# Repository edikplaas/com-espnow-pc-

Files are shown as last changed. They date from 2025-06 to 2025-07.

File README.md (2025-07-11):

# Programmes et modèles 3D en lien avec les semelles instrumentées
Dans le cadre d'un projet de recherche concernant le développement de semelles instrumentées pour la récupèration de la dynamique du bas du corps humain, ce repository est là pour comprendre et s'aider à intégrer et programmer les semelles instrumentées.  
  
Vous retrouverez dans le dossier `Documentation` tous les guides qui expliquent les différentes étapes du projet.  
Le dossier `models` contient tous les modèles 3D des semelles.  
Les dossiers `Tests ESP NOW - PC` et `Tests RS485` servent à debugger les semelles pour comprendre les différents protocoles de communication utilisés.  
Le dossier `codePlusieursPatchs` contient les programmes les plus importants.  
  
[Lien pour tous les modèles 3D sur Onshape (seulement pour consulter)](https://cad.onshape.com/documents/ade586a7c4f5538d2dbdcdd9/w/156847e7fb1b50d2fcf403ab/e/13fe36d384e4cd3dfd326341?renderMode=0&uiState=687111e13e0cfb5b92277174)

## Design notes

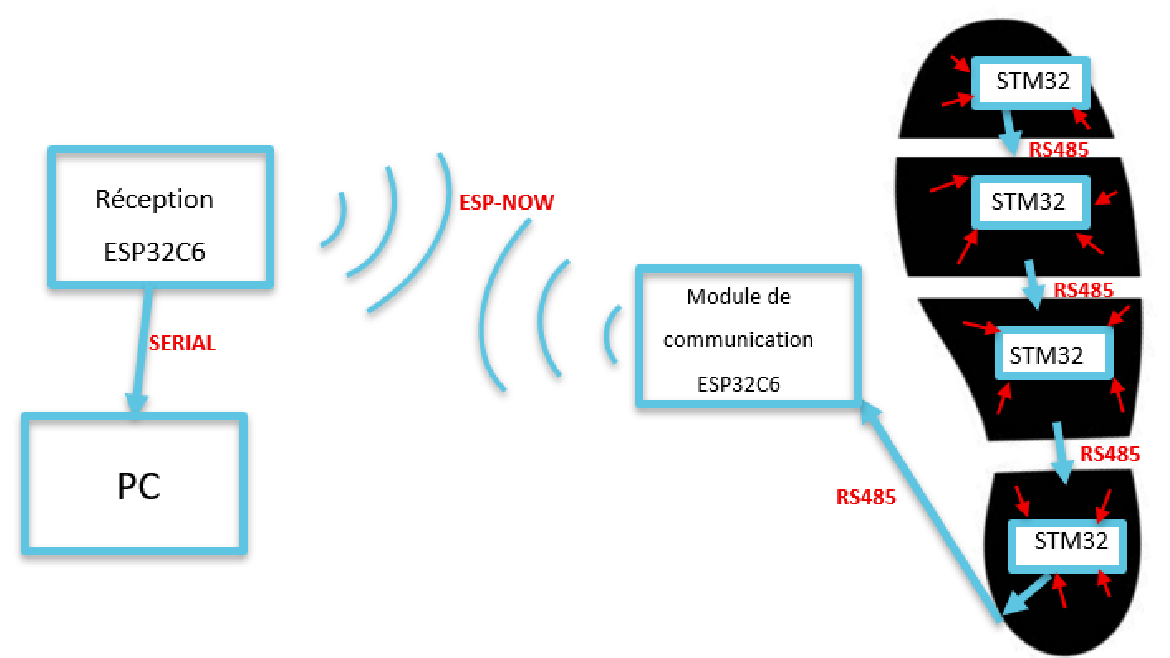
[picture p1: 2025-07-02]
Documentation/chaineCommunication.png

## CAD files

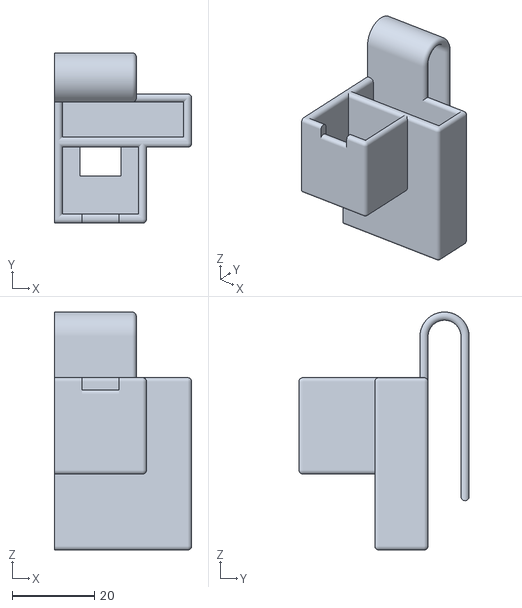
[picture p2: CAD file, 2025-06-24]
models/comModule/comModCase.stl
33.5 x 41.5 x 58.0

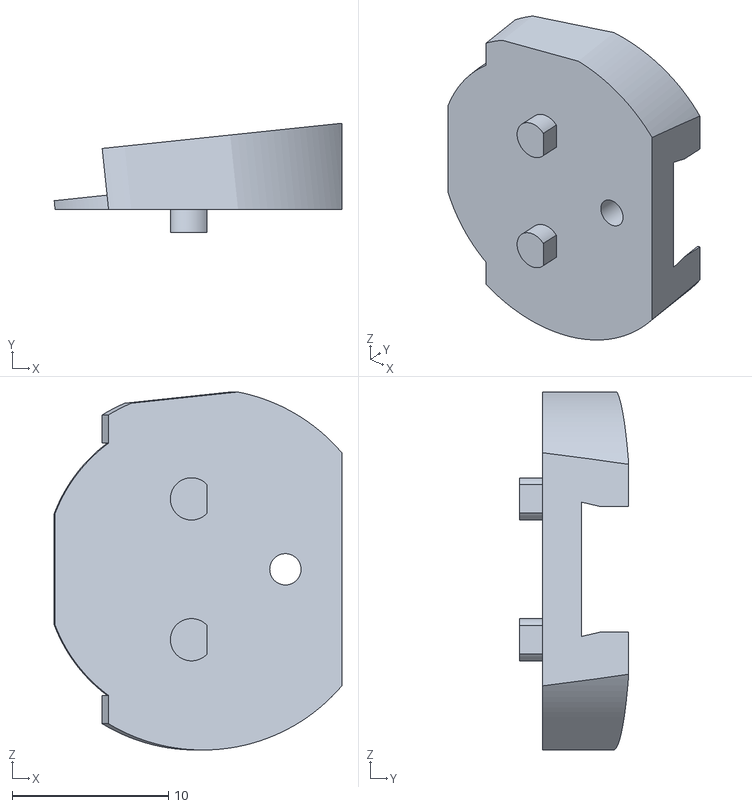
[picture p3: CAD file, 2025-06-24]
models/leftFoot/cleats/P1-heel/leftC1P1.stl
18.4 x 7.00 x 22.9

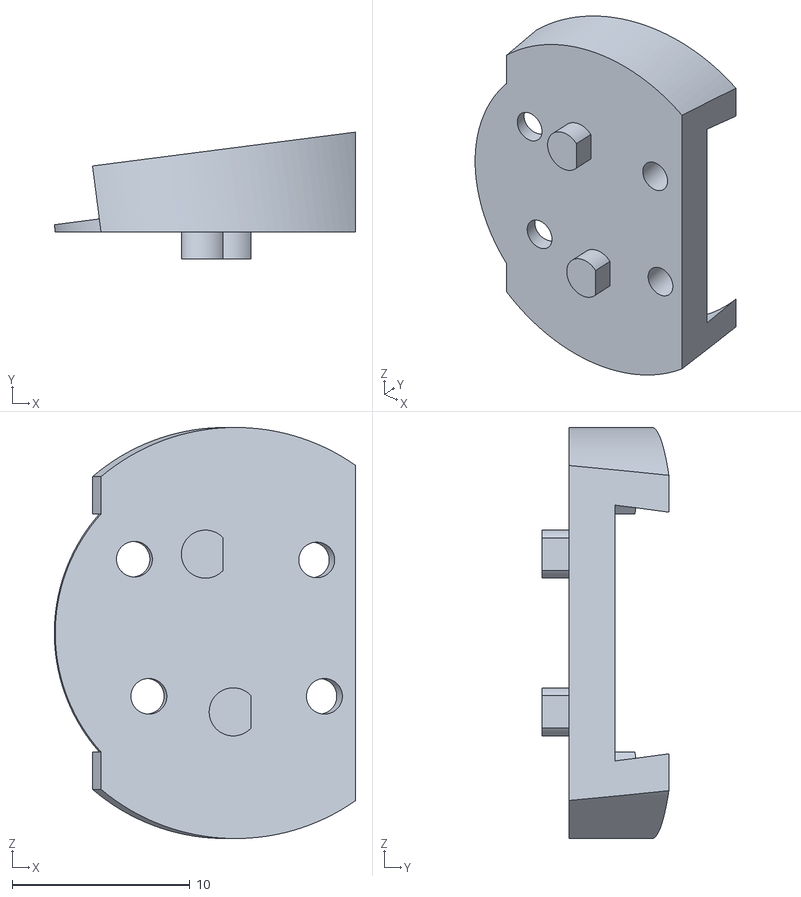
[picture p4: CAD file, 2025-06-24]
models/leftFoot/cleats/P2/leftC4P2.stl
16.9 x 7.13 x 23.1

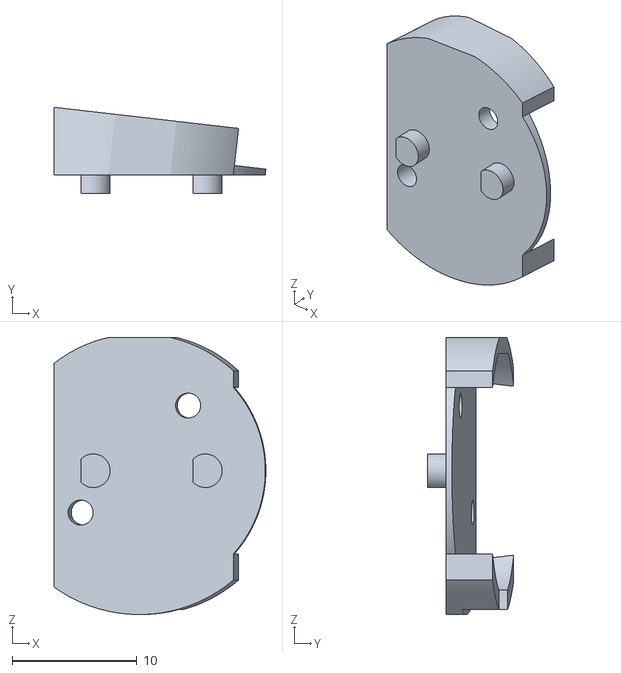
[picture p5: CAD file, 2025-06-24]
models/leftFoot/cleats/P3/leftC2P3.stl
17.0 x 6.94 x 22.2

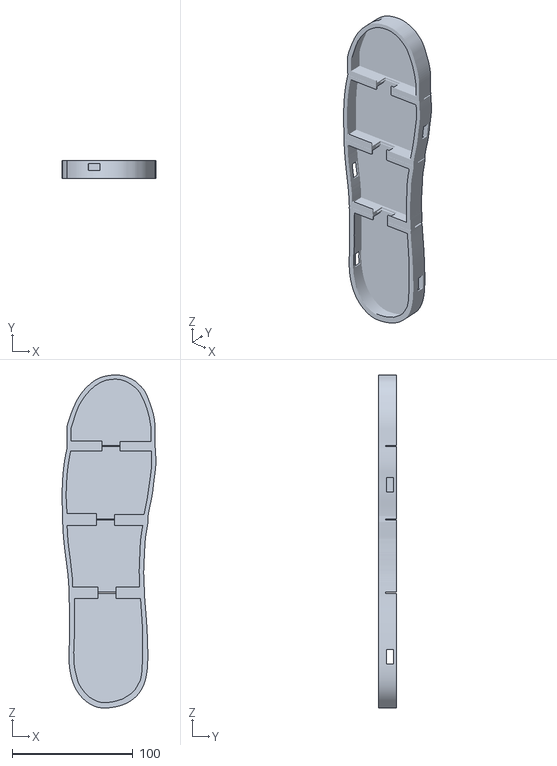
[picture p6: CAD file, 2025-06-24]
models/leftFoot/insoleCase/leftInsoleCase.stl
77.5 x 15.0 x 275.2

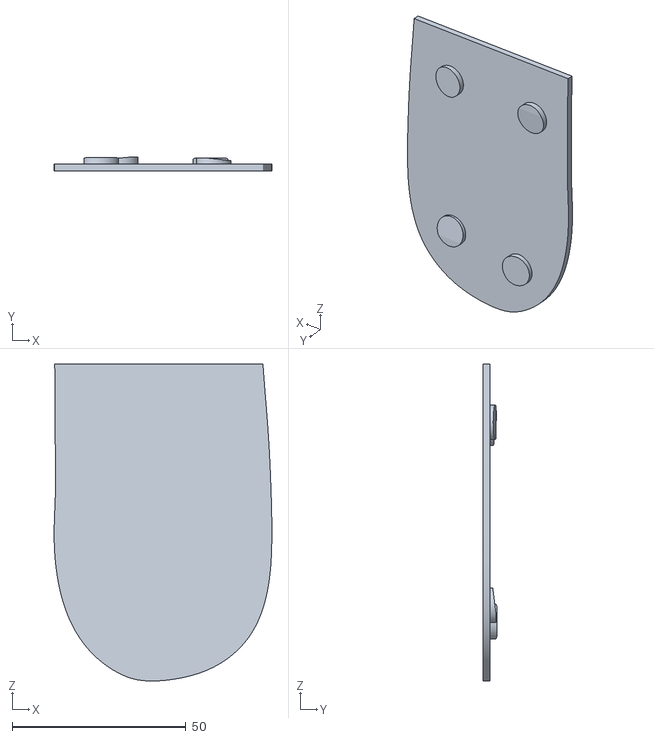
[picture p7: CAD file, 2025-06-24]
models/leftFoot/plates/leftP1-heel.stl
62.7 x 3.93 x 91.3

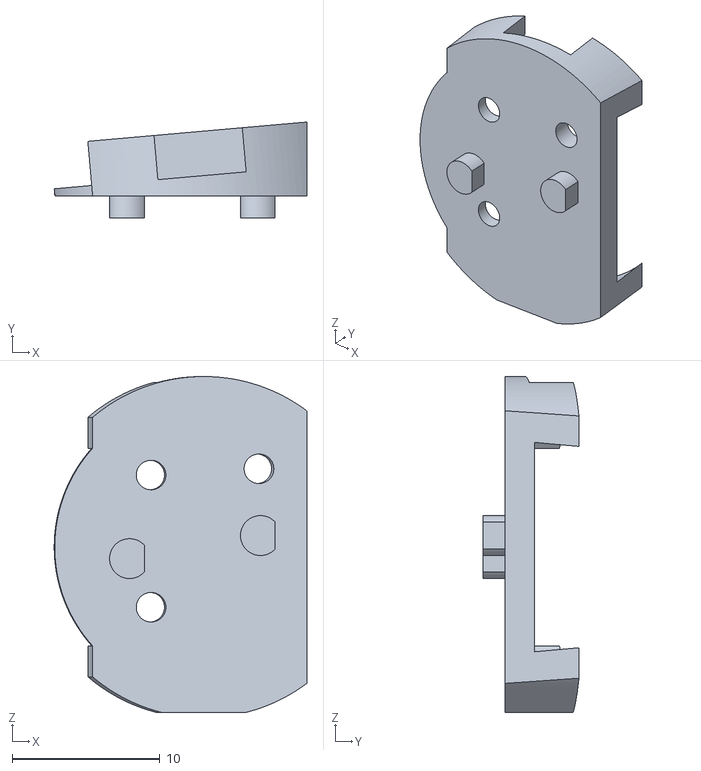
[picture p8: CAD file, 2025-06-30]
models/rightFoot/cleats/P2/rightT3P2(1).stl
17.1 x 6.50 x 22.7

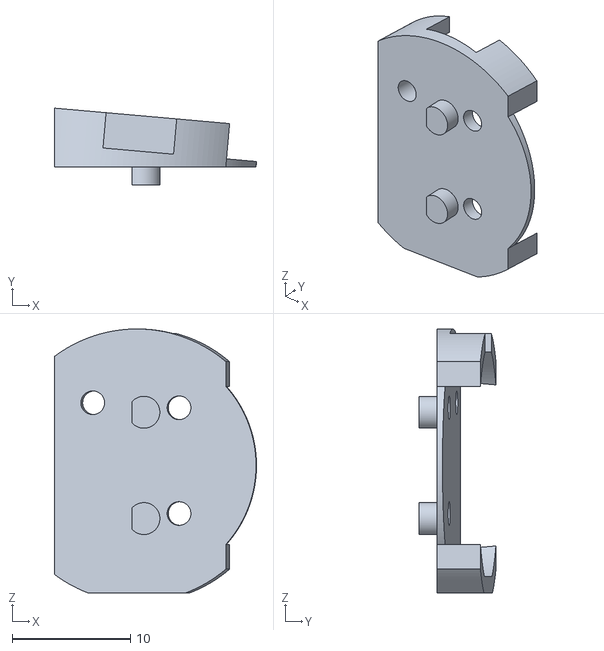
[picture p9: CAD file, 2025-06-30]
models/rightFoot/cleats/P3/rightC3P3.stl
17.1 x 6.50 x 22.3

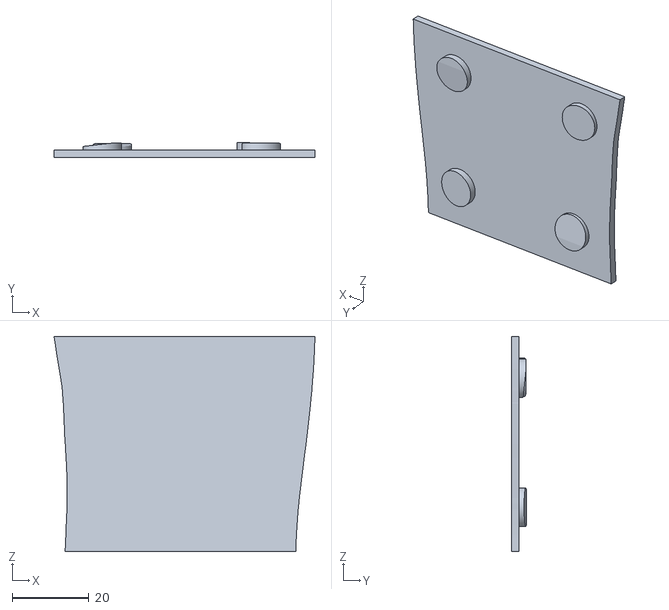
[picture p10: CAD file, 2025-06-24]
models/rightFoot/plates/rightP2.stl
67.9 x 3.93 x 56.0

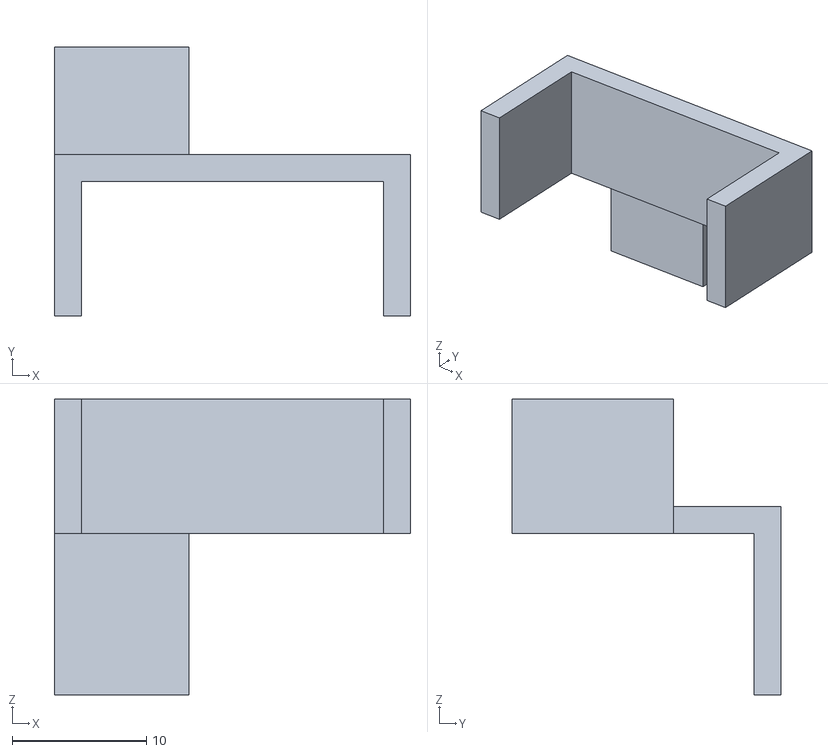
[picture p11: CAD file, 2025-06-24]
models/comModule/lid.stl
26.5 x 20.0 x 22.0

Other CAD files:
models/leftFoot/cleats/P4-toes/leftC4P1.stl
models/rightFoot/insoleCase/rightInsoleCase.stl
models/leftFoot/cleats/P2/leftC1P2.stl
models/leftFoot/cleats/P3/leftC3P3.stl
models/leftFoot/cleats/P1-heel/leftC3P1.stl
models/leftFoot/cleats/P1-heel/leftC4P1.stl
models/leftFoot/cleats/P2/leftC2P2.stl
models/leftFoot/cleats/P2/leftC3P2.stl
models/leftFoot/cleats/P3/leftC4P3.stl
models/leftFoot/cleats/P4-toes/lectC3P4.stl
models/leftFoot/plates/leftP2.stl
models/leftFoot/plates/leftP3.stl
models/leftFoot/plates/leftP4-toes.stl
models/rightFoot/cleats/P1-heel/rightC2P1.stl
models/rightFoot/cleats/P1-heel/rightC3P1.stl
models/rightFoot/cleats/P1-heel/rightC4P1.stl
models/rightFoot/cleats/P1-heel/rightCleatsP1.3mf
models/rightFoot/cleats/P2/rightC1P2.stl
models/rightFoot/cleats/P2/rightC2P2.stl
models/rightFoot/cleats/P2/rightT4P2.stl
models/rightFoot/cleats/P3/rightC2P3.stl
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

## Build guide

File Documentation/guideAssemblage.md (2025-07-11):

Ceci est le guide pour mener à bien l'assemblage des semelles instrumentées  
  
Voir photos de l'assemblage dans le dossier `Assemblage`  
  
Matériel utilisé : adhésif fin double face, fer à souder, ciseaux / cutter, flux pour la soudure, silicone en tube, objet fin (stylo).  

L'assemblage se fait dans l'ordre suivant : Fixation des taquets, soudure puis fixation des capteurs de force, soudure des patchs entre eux, pose du silicone, insertion de la semelle électronique dans la coque flexible, insertion des plaques d'appui.  
En parallèle, assemblage simple du module de communication : Insertion du microcontrôleur et de la batterie, pose du couvercle.  

## Fixer les taquets aux patchs
Avec de l'adhésif fin double face, fixez les taquets aux PCB, ne pas boucher les petits trous.  
Leur sens est important : Si le taquet a une "encoche" alors l'encoche est positionnée vers les pattes à souder.  
S'il n'y a pas d'encoche, le côté "scindé" du taquet est positionné vers les pattes à souder (voir photo).  

## Souder les capteurs de force aux PCB
Privilégier la soudure faite par un professionnel dans l'atelier électronique.  
Chaque fil d'un capteur de force se soude sur la patte en face de lui.  

## Fixer les capteurs de force aux patchs
Avec de l'adhésif fin double face, collez les capteurs dans les taquets, en poussant bien fort sur le capteur pour qu'il épouse l'inclinaison du taquet.  
Avoir les fils du capteur orientés de préférence vers les pattes.  

## Soudure des patchs entre eux
Voir photo soudure  
Souder 4 fils courts  mais assez long pour avoir un pivot faisable entre 2 patchs (longueur des fils 30 mm).  
Très important : souder les fils en croisé, et non en parallèle.  

## Pose du silicone
Avec du silicone en tube, recouvrez les soudures réalisées : sur les pattes des capteurs de force ainsi que sur les pattes entre les patchs.  
Mettre un tout petit peu de silicone, ne pas dépasser sur les bords, laisser sécher quelques heures, ne surtout pas couvrir les baromètres.  

## Insertion de la semelle électronique dans la coque flexible
Essayer de plier un peu la coque pour vous aider à insérer la semelle électronique, ne pas trop plier la semelle.  
Surtout prendre son temps.  

## Insertion des plaques d'appui
Préinsérez les plaques en les glissant sous les bords.  
Aidez-vous d'un objet fin comme un stylo pour élargir les bords de la coque et insérez les plaques.  
    
## Description des photos
1. Photo `1` : Taquets déjà fixés, capteurs soudés  
2. Photo `2` : Fixation des capteurs avec de l'adhésif double face  
3. Photo `3` : Capteurs fixés  
4. Photo `4` : Préparation des fils pour la soudure des patchs  
5. Photo `5` : Longueur des fils à couper  
6. Photo `6` : Soudure inter-patch réalisée pour un patch  
7. Photo `7` : Soudure inter-patch réalisée pour toute la semelle  
8. Photo `8` : Préparation de l'insertion de la semelle électronique  
9. Photo `9` : Insertion de la semelle électronique dans la coque flexible  
10. Photo `10` : Comparaison avec semelle terminée  
11. Photo `11` : Pose du silicone  
12. Photo `12` : Semelle assemblée avec les plaques

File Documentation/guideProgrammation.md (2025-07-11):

Ceci est le guide qui explique les différents fichiers de programmation  
Si le microcontrôleur est un ESP32 : Utiliser VSCode avec PlatformIO (en vérifiant la carte utilisée dans `platformio.ini`)  
Si le microcontrôleur est un STM32 : Utiliser Arduino IDE (pour la liaison avec CubeIDE)  
  
## Dossier "Tests RS485"
Ce dossier regroupe les fichiers de programmation qui servent à tester la communication à travers le bus RS485.  
Il y a 2 sous-dossiers : `TRANSMISSION RS485 STM32` et `LECTURE RS485 MODULE COM`.  
`TRANSMISSION RS485 STM32` : Regroupement des fichiers de programmation pour les STM32 des patchs (s'ouvre avec VSCode avec PlatformIO).  
`LECTURE RS485 MODULE COM` : Regroupement des fichiers de programmation pour l'ESP32 du module de communication (s'ouvre avec Arduino IDE).  
  
Dans ces sous-dossiers, chaque fichier de programmation correspond à une étape de test.  
`_1Octet` : Transmission / réception simple d'un octet  
`_3Octets` : Transmission / réception de 3 octets dont 2 octets d'adressage  
`_Talon4Capteurs` : Transmission / réception des données des 4 capteurs de force d'un patch  
`_Talon5CapAcc` : T/R des données des 4 capteurs de force ainsi que de l'accéléromètre dans l'IMU  
`_Talon6CapAccGy` : T/R des données des 4 capteurs de forces, accéléromètre et gyroscope de l'IMU  
`_Talon7CapAccGyBaro` : T/R de toutes les données précédentes ainsi que de la valeur brute du baromètre (pas de température ni de coefficients)  

Ces fichiers ne sont que pour la communication d'un seul patch avec le module de com, pas de toute la semelle, ils ne sont là que pour tester et comprendre la transmission et la réception de données à travers le bus RS485.  
  
## Dossier "Tests ESP NOW - PC"
Ce dossier regroupe les fichiers de programmation qui servent à tester la communication ESP NOW entre 2 ESP32 dont un qui est connecté au PC pour de la lecture via le port série.    
  
Il y a 4 fichiers de programmation : TX1, TX2, RX, RX_timestamps.  
`TX1` : Code pour l'ESP32 du module de com, envoi de 32 octets dont 2 d'adressage  
`TX2` : Code pour un potentiel deuxième module de com, envoi de 32 octets dont 2 d'adresses différents de ceux de TX1  
`RX` : Code pour l'ESP32 de la réception branché au PC, réception puis écriture sur le port série  
`RX_timestamps` : Code pour l'ESP32 de la réception branché au PC, écriture du temps écoulé entre 4 réception, sert à vérifier et optimiser la fréquence de transmission  

Attention : Vérifiez l'adresse MAC de l'ESP32 de réception, nécessaire pour la communication ESP NOW.  
  
## Dossier "codePlusieursPatchs"
Ce dossier regroupe le code "final" de tous les microcontrôleurs de la semelle.  
  
`envoi4Patchs` : Code pour chaque patch des 2 semelles, paramètrable avec le numéro du patch et l'indication de la semelle utilisée  
`lecture4Patchs` : Code de debug pour le module de com, lecture des données de toute la semelle puis écriture sur le port série (pas de communication ESP NOW), module branché au PC.  
`TX4Patchs` : Code pour les 2 modules de com, paramétrable selon la semelle utilisée  
`RX4Patchs` : Code pour l'ESP32 de réception branché au PC, réception puis écriture des données sur le port série  
`TX_ESPNOW_vide` : Code paramétrable pour les 2 modules de com, transmission de données sans semelle connectée, sert à tester la synchro des 2 semelles depuis l'ESP32 de réception.  
`getMACaddress` : Programme pour récupèrer l'adresse MAC d'un ESP32
`decodage.py` : Fichier python de traitement de données, sert surtout à compter les trames pour mesurer le taux d'erreur  
`decodageToCSV.py` : Fichier python de traitement de données, sert à mettre en forme les données, les convertir, pour les mettre dans un fichier Excel  
`envoiKeyboard.py` : Fichier python d'envoi du signal de synchronisation à l'ESP32 de réception pendant l'écriture des données.  A ne pas executer dans le terminal
`fonctionsBarometreConversion.py` : Fichier python avec les fonctions de conversion des températures et pressions brutes des baromètres, avec les coefficients intégrés 
   
## Attention 
Si vous devez à un moment changer l'ESP32, en un modèle différent tel que du l'ESP32C3 à l'ESP32C6 ou inversement, il est important de le préciser dans le fichier `platformio.ini` dans le dossier du projet en cours.  
Dans le fichier `platformio.ini`, décommentez/commentez ce qu'il vous faut :    
``` ini
; POUR ESP32C3
;[env:seeed_xiao_esp32c3]
;platform = espressif32
;board = seeed_xiao_esp32c3
;framework = arduino

; POUR ESP32C6
[env:seeed_xiao_esp32c6]
platform = https://github.com/pioarduino/platform-espressif32/releases/download/stable/platform-espressif32.zip
framework = arduino
board = seeed_xiao_esp32c6

; POUR ESP WROOM 32
;[env:nodemcu-32s]
;platform = espressif32
;board = nodemcu-32s
;framework = arduino
```
En installant PlatformIO, l'ESP32C3 est directement disponible mais pas l'ESP32C6, c'est pour ça qu'il est important de le préciser dans le fichier avec le lien GitHub.

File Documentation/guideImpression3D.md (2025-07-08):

Ceci est le guide pour mener à bien l'impression 3D de tous les éléments nécessaires aux semelles instrumentées  

"left#" => Pied gauche  
"right#" => Pied droit  
Dossier commun : models  

## Module de com :
Dossier : comModule  
Fichiers : comModCase.stl, lid.stl  
Doit être imprimé en 2 exemplaires (un pour chaque pied), épaisseur 0.20 mm standard, supports, PLA / PLA-CF.  

## Coque flexible :
Dossiers : rightFoot/insoleCase et leftFoot/insoleCase  
Fichiers : leftInsoleCase.stl et rightInsoleCase.stl  
Imprimées en TPU 95A (HF ou non), mises en diagonale du plateau, supports 40° (pour avoir des supports sous tout les bords), épaisseur 0.20 mm.  
Prendre son temps pour retirer les supports, passer un tout petit coup de décapeur pour retirer les petits fils.  

## Plaques :
Dossiers : rightFoot/plates et leftFoot/plates
Fichiers : leftP1-heel.stl, leftP2.stl, leftP3.stl, leftP4-toes.stl, rightP1-heel.stl, rightP2.stl, rightP3.stl, rightP4-toes.stl
P1 => Talon, P4 => Orteils  
Doivent être imprimées à plat, pas de supports, épaisseur 0.08 mm de préférence, peuvent être imprimées directement par 4 (pied gauche puis pied droit), PLA / PLA-CF.  

## Taquets:
Dossier : rightFoot/cleats et leftFoot/cleats  
Doivent être imprimés en utilisant l'option mise à plat sur plateau, pas de supports, 0.08 mm d'épaisseur, impression de 3 taquets en même temps au maximum sinon grand risque d'échec d'impression, PLA.  
Attention à bien isoler les taquets après l'impression pour ne pas les mélanger (lot de taquets pour le talon, un autre pour les orteils etc.).

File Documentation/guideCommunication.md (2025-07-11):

## Guide pour comprendre les différents bus et protocoles de communication utilisés  

=> Voir photo de chaîne de communication  

Sur chaque patch se trouve un microcontrôleur STM32, ce microcontrôleur peut communiquer vers un autre composant en liaison série avec les broches RX/TX.  
Nous utilisons cette liaison RX/TX pour convertir cette liaison série en liaison RS485 grâce à un convertisseur UART / RS485.  
Ce bus RS485 nous permet d'avoir une communication multipoint, rapide, le tout sur une longue distance.  

4 STM32 des 4 patchs ainsi que l'ESP32 du module de communication se trouvent sur le bus RS485. C'est donc 5 composants qui communiquent entre eux grâce à ce bus.  
Néamoins, il faut faire attention à comment nous programmons avec ce bus RS485, en effet quand un des composants "parle" (ou écrit) sur ce bus, il faut que tous les autres composants soient en mode "écoute".  

## Code exemple d'envoi d'un nombre (pour STM32)
``` c
LL_GPIO_SetOutputPin(GPIOB, LL_GPIO_PIN_3); //DE : high, RE : low.1  
Serial.write(nombre);  
Serial.flush();  
LL_GPIO_ResetOutputPin(GPIOB, LL_GPIO_PIN_3); 
```

La première ligne sert à mettre le convertisseur UART / RS485 en mode écriture (il faut veiller à ce que tous les autres composants soient en mode lecture).  
On utilise `Serial.write(nombre)` pour envoyer une donnée, ou bien `Serial.write(trame,tailleDeTrame)` pour envoyer une trame de données.  
'Serial.flush()' est utilisé pour s'assurer que les données sont envoyées sur la liaison série.  
Puis la dernière ligne sert à activer le mode lecture.  

## Alternative (pour ESP32)
```c
digitalWrite(DE_RE_PIN, HIGH); // Mode transmission  
Serial0.write(100);            // Octet spécial pour le top départ  
Serial0.flush(); // SERIAL2 POUR LE PIED DROIT ET SERIAL0 POUR LE PIED GAUCHE  
digitalWrite(DE_RE_PIN, LOW); // Mode réception  
```

## Comment les microcontrôleurs communiquent entre eux ?
Pour que le module de communication récupère toutes les données de la semelle pour ensuite les envoyer vers le PC, il envoie un signal "top départ" (ici un nombre sur un octet) sur le bus RS485, les 4 STM32 étant en mode écoute, ils commutent en mode écriture après avoir reçu le top départ.  
Mais attention : chaque STM32 possède un délai propre à leur numéro de patch, cela veut dire que c'est en premier le talon qui passe en mode écriture pour envoyer les données de la semelle, en un temps inférieur à 100µs. Après le délai imposé pour le deuxième patch, c'est à son tour d'envoyer ses données, ainsi de suite.  
Donc pour avoir une fréquence de communication de 250 Hz, le module de communication envoie son top départ toutes les 4000 µs.  

### Etapes lors de la communication
1. Les semelles sont allumées, rien ne se passe.  
2. L'ESP32 de réception est alimenté.  
3. 5 secondes plus tard, l'ESP32 de réception envoie aux 2 modules de communication un signal top départ (un octet).  
4. Après avoir reçu ce signal, les ESP32 des modules de communication peuvent commencer, ils envoient alors un signal top départ aux 4 patchs en même temps.  
5. Ces 4 patchs étaient en mode lecture, maintenant qu'ils ont tous reçu le signal, le patch du talon commute en mode écriture, envoie toutes ses données sur le bus RS485 et recommute en mode lecture.  
6. Le patch suivant écris ses données à son tour, et ainsi de suite pour les 4 patchs de la semelle, chaque patch attend un temps différent pour garder un bon ordre des trames reçues.  
7. Pendant que les 4 patchs écrivent leurs données, le module de communication récupère les 4 trames, et une fois les 4 trames récoltées il les envoie en sans-fil avec le protocole ESP-NOW vers le module de réception.  
8. Le module de communication recommence à envoyer le top départ à une fréquence précise, on a donc l'acquisition des données en continu.  
9. Le module de réception reçoit ses trames, les stocke et les écris directement sur le bus USB vers le PC.  
10. Sur le PC, les données qui arrivent sont directement enregistrées dans un fichier binaire.  
  
## Code d'envoi des données avec un délai propre au patch
```c
void loop() {  
  byte octet = 0;  
  while (octet != 100) { // Attente de la détection du top départ envoyé par le module de com  
    if (Serial.available()) { // Si des données disponibles  
      octet = Serial.read(); // On lit l'octet  
    }
  }
  delayMicroseconds(300 + 100 * (patch)); // Délai imposé pour respecter la commutation du mode transmission au mode réception  
  read_send_data();  
}  
```
Le module de communication, après avoir reçu les 4 trames de données (une de chaque patch), envoie d'un coup les 4 trames en sans-fil vers un autre ESP32 connecté au PC grâce au protocole ESP-NOW.    

## Trame d'une semelle
La trame d'une semelle entière reçue sur le PC se décompose sous cette forme :  
signal-ID1(talon)-ID2-CPT-F1-F2-F3-F4-accX-accY-accZ-gyX-gyY-gyZ-press-temp-x0-x1-y0-y1-z0-z1-xyz_ext-  
ID1(patch 2) -ID2-CPT-F1-F2-F3-F4-accX-accY-accZ-gyX-gyY-gyZ-press-temp-x0-x1-y0-y1-z0-z1-xyz_ext-  
ID1(patch 3)-ID2-CPT-F1-F2-F3-F4-accX-accY-accZ-gyX-gyY-gyZ-press-temp-x0-x1-y0-y1-z0-z1-xyz_ext-  
ID1(patch 4)-ID2-CPT-F1-F2-F3-F4-accX-accY-accZ-gyX-gyY-gyZ-press-temp-x0-x1-y0-y1-z0-z1-xyz_ext-timestamp  
  
Où :  
`signal` (uint8_t) correspond au signal de synchro envoyé depuis le programme python `envoiKeyboard.py` 
`ID1` et `ID2` (2x uint8_t) les identifiants de la trame  
`CPT` (uint8_t) le compteur interne d'un patch  
`F1`, `F2`, `F3` et `F4` (4x uint16_t) les forces brutes des capteurs de force
`accX`, `accY`, `accZ`, `gyX`, `gyY` et `gyZ` (6x int16_t) les données brutes de l'IMU  
`press` et `temp` (2x 3 octets, donc 2x 24 bits, attention à la conversion) la pression atmosphérique brute et la température brute du baromètre  
`x0`, `x1`, `y0`, `y1`, `z0`, `z1` et `xyz_ext` (7x uint8_t) les données du magnétomètre  
`timestamp` (uint32_t) le temps écoulé entre 2 réceptions de trame d'une semelle entière  
  
La trame entière d'une semelle fait donc  1+36x4+4 =  149 octets.  
Dans 1+36x4+4, 1 correspond à l'octet du signal du programme python, le 36x4 correspond aux 4 trames des patchs et le +4 correspond à l'uint32_t timestamp  

## Identifiants de trame
Les identifiants de trame de chaque patch possède en début de trame une paire d'identifiants (2 octets).  
Cette paire est sous la forme ID1, ID2.  
Patch 1 talon gauche : ID1 = 0x01, ID2 = 0x02  
Patch 2 (après talon): ID1 = 0x03, ID2 = 0x04  
Patch 3 : ID1 = 0x05, ID2 = 0x06  
Patch 4 orteils gauche : ID1 = 0x07, ID2 = 0x08  
  
Patch 1 talon droit : ID1 = 0x09, ID2 = 0x0A  
Patch 2 (après talon) : ID1 = 0x0B, ID2 = 0x0C  
Patch 3 : ID1 = 0x0D, ID2 = 0x0E  
Patch 4 orteils droit : ID1 = 0x0F, ID2 = 0x10 (16)

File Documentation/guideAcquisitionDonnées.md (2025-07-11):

Ceci est le guide qui explique l'acquisition des données d'une ou plusieurs semelles
  
## Etapes
  
Pour acquérir les données des semelles, procédez de cette manière :  
1. Allumer les 2 semelles (peu importe l'ordre)  
2. Brancher au PC l'ESP32 de réception (privilégiez un cable court)  
3. Ecrivez la commande d'acquisition des données dans un terminal (voir partie commandes)  
4. Attendre que les données s'affichent (< 5 secondes)  
5. Faites CTRL+A puis CTRL+Q dans le terminal pour arrêter l'acquisition des données  
6. Convertissez vos données en lançant le programme python decodageToCSV.py (voir partie commandes)  

## Commandes
  
Installez picocom  
Dans un terminal, allez de préférence dans /com-espnow-pc/codePlusieursPatchs/  
Ecrivez la ligne suivante : `picocom -b 921600 /dev/ttyUSB0 --log dataSemelle.bin`  
`921600` correspond au baud rate, mettez celui présent dans le code RX4Patchs (921600 pour l'ESP WROOM 32 et 2000000 pour l'ESP32C3).  
`/dev/ttyUSB0` est le port USB utilisé. Si vous cherchez le port utilisé par l'ESP32 de réception, faites cette commande après avoir branché l'ESP32 : `ls /dev/ttyACM* /dev/ttyUSB**`  
`dataSemelle.bin` est le fichier binaire créé qui contient toutes les données à acquérir, vous pouvez le renommer comme vous voulez.  
Faites CTRL+A puis CTRL+Q dans le terminal pour arrêter l'acquisition des données.  
  
Pour convertir les données acquises, executez le programme decodageToCSV.py dans le terminal.  
L'appel possède des arguments : input_file et output_file qui correspondent au fichier d'entrée et au fichier de sortie respectivement.  
Exemple d'appel : `python3 decodageToCSV.py dataSemelleEXEMPLE.bin feuilleOutputEXEMPLE.csv`  
Faites attention au chemin du fichier, dans l'exemple le fichier d'entrée est situé dans le même dossier que le programme python, et le fichier de sortie est créé dans le même dossier.  

## Bugs
  
Si jamais l'acquisition des données ne se fait pas, vérifiez le baud rate utilisé en consultant le programme `RX4Patchs`, vous pouvez également vérifier le niveau de charge des batteries.  
Si des pauses apparaissent dans l'acquisition des données, baissez la fréquence.  
Si des trames n'apparaissent finalement pas dans la feuille .CSV finale (par exemple les orteils gauche), c'est peut être qu'un patch s'est déssoudé.

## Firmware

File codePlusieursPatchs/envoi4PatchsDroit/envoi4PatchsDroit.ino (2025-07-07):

#include <SPI.h>
#define DE_RE_PIN PB3

#define SCL_1_PIN LL_GPIO_PIN_8 //PA8 //d9
#define SDA_1_PIN LL_GPIO_PIN_9 //PA9 //d1

#define SDA_2_PIN LL_GPIO_PIN_10 //PA10 //d0
#define SDA_3_PIN LL_GPIO_PIN_1 //PA1 //a1
#define SDA_4_PIN LL_GPIO_PIN_0 //PA0 //a0


#define MOSI_PIN PA7 // MOSI Pin A6
#define MISO_PIN PA6 // MISO Pin A5
#define SCLK_PIN PA5 // Clock Pin A4 


#define CS_acc PB1   // Chip Select or Slave Select Pin D6
#define CS_baro PA4   // Chip Select or Slave Select Pin A3
#define CS_mag PA3

uint8_t patch = 4; // Patch 1 = Talon, Patch 4 = Orteils
uint8_t ADDRESS_DEBUT1 = 9 + 2 * (patch - 1); // Identifiant 1 dans l'entête, directement calculé à partir du numéro du patch
uint8_t ADDRESS_DEBUT2 = 10 + 2 * (patch - 1); // Identifiant 2 dans l'entête, directement calculé à partir du numéro du patch
uint8_t frameCounter = 0; // Compteur interne à la trame

void setup() {
  Serial.begin(2000000);
  SPI.setSCLK(SCLK_PIN);
  SPI.setMOSI(MOSI_PIN);
  SPI.setMISO(MISO_PIN);
  SPI.begin();
  pinMode(CS_acc, OUTPUT);
  digitalWrite(CS_acc, HIGH);
  pinMode(CS_baro, OUTPUT);
  digitalWrite(CS_baro, HIGH);
  pinMode(CS_mag, OUTPUT);
  digitalWrite(CS_mag, HIGH);
  //config imu
  writeRegister16(0x20, 0x40, 0x27); //acc
  writeRegister16(0x21, 0x40, 0x4B); //gyr
  //config baro
  writeRegister8(0x1B, 0x33); //(Normal mode, pressure enabled, temperature enabled), reg = pwr_ctrl
  writeRegister8(0x1C, 0x00); //resolution *1, reg = OSR
  initializeMMC5983MA();
  pinMode(DE_RE_PIN, OUTPUT);
  digitalWrite(DE_RE_PIN, LOW); // Mode réception activé
}
void loop() {
  byte octet = 0;
  while (octet != 100) { // Attente de la détection du top départ envoyé par le module de com
    if (Serial.available()) { // Si des données disponibles
      octet = Serial.read(); // On lit l'octet
    }
  }
  delayMicroseconds(300 + 100 * (patch)); // Délai imposé pour respecter la commutation du mode transmission au mode réception, et également l'ordre d'envoi des données selon le numéro de patch (ordre 1 2 3 4)
  read_send_data();
}
void read_send_data() {
  uint8_t frame[36];
  frame[0] = ADDRESS_DEBUT1;
  frame[1] = ADDRESS_DEBUT2;
  frame[2] = frameCounter++;

  uint8_t data_1[2], data_2[2], data_3[2], data_4[2];
  uint8_t data_press[3];
  uint8_t data_temp[3];
  int bytesRead_1 = I2CRead_new(0x28, data_1, data_2, data_3, data_4, sizeof(data_1));


  int bridge_data_1 = (data_1[0] << 8) | data_1[1];
  int force_1 = (bridge_data_1 & 0x3FFF);

  int bridge_data_2 = (data_2[0] << 8) | data_2[1];  // decaler msb et combiner avc lsb
  int force_2 = (bridge_data_2 & 0x3FFF); //masquer pr garder que les bits de 0-13

  int bridge_data_3 = (data_3[0] << 8) | data_3[1];  // decaler msb et combiner avc lsb
  int force_3 = (bridge_data_3 & 0x3FFF); //masquer pr garder que les bits de 0-13

  int bridge_data_4 = (data_4[0] << 8) | data_4[1];  // decaler msb et combiner avc lsb
  int force_4 = (bridge_data_4 & 0x3FFF); //masquer pr garder que les bits de 0-13

  uint16_t rawAccX = read16bitRegister(0x03); // Read X-axis accelerometer
  uint16_t rawAccY = read16bitRegister(0x04); // Read Y-axis accelerometer
  uint16_t rawAccZ = read16bitRegister(0x05); // Read Z-axis accelerometer

  uint16_t rawGyrX = read16bitRegister(0x06); // Read X-axis gyroscope
  uint16_t rawGyrY = read16bitRegister(0x07); // Read Y-axis gyroscope
  uint16_t rawGyrZ = read16bitRegister(0x08); // Read Z-axis gyroscope

  readMultipleRegisters(0x04, data_press, 3); //la data pressure commence a partir de ce registre
  uint32_t pressure = ((uint32_t)data_press[2] << 16) | ((uint32_t)data_press[1] << 8) | data_press[0];
  readMultipleRegisters(0x07, data_temp, 3);
  uint32_t temp = ((uint32_t)data_temp[2] << 16) | ((uint32_t)data_temp[1] << 8) | data_temp[0]; //raw temp

  uint8_t x0 = readRegister(0x00);
  uint8_t x1 = readRegister(0x01);
  uint8_t y0 = readRegister(0x02);
  uint8_t y1 = readRegister(0x03);
  uint8_t z0 = readRegister(0x04);
  uint8_t z1 = readRegister(0x05);
  uint8_t xyz_ext = readRegister(0x06);

  switch (patch) {
    case 1:
      frame[3] = (force_3 >> 8) & 0xFF; // Décomposition des octets
      frame[4] = force_3 & 0xFF;
      frame[5] = (force_1 >> 8) & 0xFF;
      frame[6] = force_1 & 0xFF;
      frame[7] = (force_4 >> 8) & 0xFF;
      frame[8] = force_4 & 0xFF;
      frame[9] = (force_2 >> 8) & 0xFF;
      frame[10] = force_2 & 0xFF;
      break;
    case 2 :
      frame[3] = (force_3 >> 8) & 0xFF; // Décomposition des octets
      frame[4] = force_3 & 0xFF;
      frame[5] = (force_2 >> 8) & 0xFF;
      frame[6] = force_2 & 0xFF;
      frame[7] = (force_4 >> 8) & 0xFF;
      frame[8] = force_4 & 0xFF;
      frame[9] = (force_1 >> 8) & 0xFF;
      frame[10] = force_1 & 0xFF;
      break;
    case 3 :
      frame[3] = (force_3 >> 8) & 0xFF; // Décomposition des octets
      frame[4] = force_3 & 0xFF;
      frame[5] = (force_1 >> 8) & 0xFF;
      frame[6] = force_1 & 0xFF;
      frame[7] = (force_4 >> 8) & 0xFF;
      frame[8] = force_4 & 0xFF;
      frame[9] = (force_2 >> 8) & 0xFF;
      frame[10] = force_2 & 0xFF;
      break;
    case 4:
      frame[3] = (force_3 >> 8) & 0xFF; // Décomposition des octets
      frame[4] = force_3 & 0xFF;
      frame[5] = (force_1 >> 8) & 0xFF;
      frame[6] = force_1 & 0xFF;
      frame[7] = (force_4 >> 8) & 0xFF;
      frame[8] = force_4 & 0xFF;
      frame[9] = (force_2 >> 8) & 0xFF;
      frame[10] = force_2 & 0xFF;
  }


  frame[11]  = (rawAccX >> 8) & 0xFF;
  frame[12]  = rawAccX & 0xFF;
  frame[13] = (rawAccY >> 8) & 0xFF;
  frame[14] = rawAccY & 0xFF;
  frame[15] = (rawAccZ >> 8) & 0xFF;
  frame[16] = rawAccZ & 0xFF;
  frame[17] = (rawGyrX >> 8) & 0xFF;
  frame[18] = rawGyrX & 0xFF;
  frame[19] = (rawGyrY >> 8) & 0xFF;
  frame[20] = rawGyrY & 0xFF;
  frame[21] = (rawGyrZ >> 8) & 0xFF;
  frame[22] = rawGyrZ & 0xFF;

  frame[23] = (pressure >> 16) & 0xFF;
  frame[24] = (pressure >> 8) & 0xFF;
  frame[25] = pressure & 0xFF;
  frame[26] = (temp >> 16) & 0xFF;
  frame[27] = (temp >> 8) & 0xFF;
  frame[28] = temp & 0xFF;

  frame[29] = x0;
  frame[30] = x1;
  frame[31] = y0;
  frame[32] = y1;
  frame[33] = z0;
  frame[34] = z1;
  frame[35] = xyz_ext;
  LL_GPIO_SetOutputPin(GPIOB, LL_GPIO_PIN_3); //DE : high, RE : low.1
  Serial.write(frame, 36);
  Serial.flush();
  LL_GPIO_ResetOutputPin(GPIOB, LL_GPIO_PIN_3);
}


void readMultipleRegisters(uint8_t startReg, uint8_t *data, uint8_t count) {

  digitalWrite(CS_baro, LOW);  // Select the BMP384

  SPI.transfer(startReg | 0x80);   // Send start register address with read bit (bit 7 set to 1)

  SPI.transfer(0x00);         // Send dummy byte
  for (uint8_t i = 0; i < count; i++) {
    data[i] = SPI.transfer(0x00);  // Read the data bytes
  }
  digitalWrite(CS_baro, HIGH);  // Deselect the BMP384
}

//read 2 bytes
uint16_t read16bitRegister(uint8_t reg) {

  digitalWrite(CS_acc, LOW);  // Select the BMI323
  SPI.transfer(reg | 0x80);   // Send register address with read command (bit 7 set)

  SPI.transfer(0x00); //dummy read
  uint8_t lowByte = SPI.transfer(0x00);  //P22, accelerometer, P23, gyroscope
  uint8_t highByte = SPI.transfer(0x00);

  uint16_t value = (highByte << 8) | lowByte;  // Read 16 bits (2 bytes)
  digitalWrite(CS_acc, HIGH);  // Deselect the BMI323
  return value;
}

//read 1 byte
uint16_t read8bitRegister(uint8_t reg) {

  SPI.transfer(reg | 0x80);   // Send register address with read command (bit 7 set)

  SPI.transfer(0x00); //dummy read

  uint16_t value = SPI.transfer(0x00);
  return value;
}

//write 2 bytes
void writeRegister16(byte address, uint16_t value1, uint16_t value2) {
  digitalWrite(CS_acc, LOW);  // Select the sensor

  uint16_t addr = address & 0x7F;

  // Send the register address
  SPI.transfer(addr);

  uint16_t value = (value2 << 8) | value1; // decaler msb et combiner avc lsb
  SPI.transfer16(value);

  digitalWrite(CS_acc, HIGH);  // Deselect the sensor

}


//write 1 byte
void writeRegister8(byte address, uint16_t value) {
  digitalWrite(CS_baro, LOW);  // Select the sensor

  uint16_t ctrl = address & 0x7F;

  // Send the register address
  SPI.transfer(ctrl);

  SPI.transfer(value);

  digitalWrite(CS_baro, HIGH);  // Deselect the sensor

}


void initializeMMC5983MA() {
  writeRegister(0x0A, 0b00000011);  // Bande passante : 0.5ms (800Hz) → BW1=1, BW0=1
  writeRegister(0x09, 0b00100000);  // Auto-Set activé
  writeRegister(0x0B, 0b10011111);   //  Mode mesure continue à 1000 Hz (CM_freq=111), Set automatique tous les 75 échantillons (Prd_set=001),Bit 7 = En_prd_set, bit 3 = Cmm_en

  delay(10);
}

void writeRegister(uint8_t reg, uint8_t value) {
  //SPI.beginTransaction(SPISettings(1000000, MSBFIRST, SPI_MODE0));
  digitalWrite(CS_mag, LOW);
  SPI.transfer((reg & 0x3F) | 0x00);  // Write: MSB = 0
  SPI.transfer(value);
  digitalWrite(CS_mag, HIGH);
  //SPI.endTransaction();
}

uint8_t readRegister(uint8_t reg) {
  //SPI.beginTransaction(SPISettings(1000000, MSBFIRST, SPI_MODE0));
  digitalWrite(CS_mag, LOW);
  SPI.transfer((reg & 0x3F) | 0x80);  // Read: MSB = 1
  uint8_t value = SPI.transfer(0x00);
  digitalWrite(CS_mag, HIGH);
  //SPI.endTransaction();
  return value;
}

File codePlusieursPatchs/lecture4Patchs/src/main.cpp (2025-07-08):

#include <Arduino.h>

/*
Code de debug sans communication ESPNOW, c'est directement le module de communication de la semelle qui communique avec le PC via le port série

La communication se passe de cette manière :
L'ESP du module de com envoie un "top départ" (un octet spécial) aux 4 patchs à une fréquence précise
A chaque fois que les 4 patchs reçoivent le top départ, ils envoient leurs données en respectant l'ordre patch 1 - 2 - 3 - 4 à l'aide d'un délai appliqué avant la transmission
Chaque trame est lue, mais l'envoi sans fil en ESP NOW se fait que lorsque les 4 trames des patchs sont reçues et stockées pour éviter de saturer la com ESP NOW tout en respectant
la fréquence de 250Hz
*/

#define DE_RE_PIN 1                               // GPIO1 pour contrôler DE/RE du transceiver RS485
const unsigned long intervalleTopDepart = 20000; // intervalle en µs qui correspond à la période entre chaque envoi du top départ qui permet de récupèrer les 4 trames respectives des patchs
// 4000 µs => 250 Hz

typedef struct struct_message
{ // Trame unique de 36 octets de data
  uint8_t bytes[36];
} struct_message;

typedef struct struct_combined_message
{                     // Grosse trame combinée de 4 trames (les 4 patchs) pour l'envoi en ESP NOW
  uint8_t bytes[144]; // 36 octets * 4 trames
} struct_combined_message;

struct_combined_message combinedData;
int trameCount = 0; // Compteur pour le nombre de trames stockées
int16_t mx, my, mz;

void envoiTopDepart() // Fonction pour l'envoi du top départ aux 4 patchs
{
  static int oldTime = 0;
  int newTime = micros();
  if (newTime - oldTime >= intervalleTopDepart)
  { // Envoi du top départ à 250 Hz (période 4000µs)
    oldTime = newTime;
    digitalWrite(DE_RE_PIN, HIGH); // Mode transmission
    Serial2.write(100);            // Octet spécial pour le top départ
    Serial2.flush();               // SERIAL2 POUR LE PIED DROIT ET SERIAL0 POUR LE PIED GAUCHE
    digitalWrite(DE_RE_PIN, LOW);  // Mode réception
  }
}

void setup()
{
  Serial.begin(2000000);
  Serial0.begin(2000000);
  Serial2.begin(2000000);
  pinMode(DE_RE_PIN, OUTPUT); // Configurer GPIO1 comme sortie
  delay(100);
}

void loop()
{
  static int cpt;
  if (Serial0.available()) // Si il y a des données dispo à la lecture et que l'ESP n'est pas branché au PC
  {                        // On lit les données et on les stocke
    byte headers[2];       // Récupère l'entête (2 octets)
    Serial0.readBytes(headers, 2);

    int trameType = -1;
    // DECOMMENTER / COMMENTER CE QUE VOUS VOULEZ 
    /*
    if (headers[0] == 1 && headers[1] == 2)
      trameType = 0; // Identification du patch
     if (headers[0] == 3 && headers[1] == 4)
      trameType = 1;
     if (headers[0] == 5 && headers[1] == 6)
      trameType = 2;
     if (headers[0] == 7 && headers[1] == 8)
      trameType = 3;
      cpt++;
    */
    //if (headers[0] == 9 && headers[1] == 10)
    //  trameType = 0; // Identification du patch
    //if (headers[0] == 11 && headers[1] == 12)
    //  trameType = 1;
   // if (headers[0] == 13 && headers[1] == 14)
   //   trameType = 2;
    if (headers[0] == 15 && headers[1] == 16)
      trameType = 3;
    cpt++;
    if (trameType != -1)
    {
      byte data[34];
      Serial0.readBytes(data, 34); // Lecture des 34 octets de data après l'entête
      trameCount++;
      // COMMENTEZ / DECOMMENTEZ CE QUE VOUS VOULEZ POUR DEBUG
      /*
      uint32_t press = (data[21] << 16 | data[22] << 8) | data[23];
      uint32_t temp = (data[24] << 16 | data[25] << 8) | data[26];
      Serial.print(headers[0], HEX);
      Serial.print(" ");
      Serial.print(headers[1], HEX);
      Serial.print(" ");
      Serial.print(press);
      Serial.print(" ");
      Serial.println(temp);
      */

      Serial.print(headers[0], HEX);
      Serial.print(" ");
      Serial.print(headers[1], HEX);
      Serial.print(" ");

      int force1 = data[1] << 8 | data[2];
      int force2 = data[3] << 8 | data[4];
      int force3 = data[5] << 8 | data[6];
      int force4 = data[7] << 8 | data[8];
      int16_t accX = data[9] << 8 | data[10];
      int16_t accY = data[11] << 8 | data[12];
      int16_t accZ = data[13] << 8 | data[14];
      int16_t gyX = data[15] << 8 | data[16];
      int16_t gyY = data[17] << 8 | data[18];
      int16_t gyZ = data[19] << 8 | data[20];

      Serial.print(force1);
      Serial.print(" ");
      Serial.print(force2);
      Serial.print(" ");
      Serial.print(force3);
      Serial.print(" ");
      Serial.println(force4);
      /*
      Serial.print(" ");
      Serial.print(accX);
      Serial.print(" ");
      Serial.print(accY);
      Serial.print(" ");
      Serial.print(accZ);
      Serial.print(" ");
      Serial.print(gyX);
      Serial.print(" ");
      Serial.print(gyY);
      Serial.print(" ");
      Serial.print(gyZ);
      uint32_t press = (data[21] << 16 | data[22] << 8) | data[23];
      Serial.print(" ");
      Serial.print(press);
      Serial.println(" ");
      */

      /*
      uint8_t x0 = data[27];
      uint8_t x1 = data[28];
      uint8_t y0 = data[29];
      uint8_t y1 = data[30];
      uint8_t z0 = data[31];
      uint8_t z1 = data[32];
      uint8_t xyz_ext = data[33];
      uint32_t x_raw = ((uint32_t)x0 << 10) | ((uint32_t)x1 << 2) | ((xyz_ext >> 6) & 0x03);
      uint32_t y_raw = ((uint32_t)y0 << 10) | ((uint32_t)y1 << 2) | ((xyz_ext >> 4) & 0x03);
      uint32_t z_raw = ((uint32_t)z0 << 10) | ((uint32_t)z1 << 2) | ((xyz_ext >> 2) & 0x03);
      mx = (int32_t)x_raw - 131072; // raw values
      my = (int32_t)y_raw - 131072;
      mz = (int32_t)z_raw - 131072;
      float fx = mx * 0.00625f; // en microteslas sinon *0.0625f;  pour mG milligauss
      float fy = my * 0.00625f;
      float fz = mz * 0.00625f;
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

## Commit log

2025-05-21 Changement de nom du programme Python et suppression du délais pour les programmes de transmission
2025-05-21 Modification de TX1, TX2 et RX pour une transmission de 100Hz, utilisation d'un buffer pour l'envoi des données vers Python
2025-05-21 Fréquence de transmission ajustée à 500Hz, calcul de la fréquence de réception sur Python
2025-05-21 Transmission 500Hz, 100 octets envoyés, code python adapté
2025-05-22 Transmission de 30 octets d'un coup à 500Hz, 2 programmes python différents (1 pour la com PC, 1 avec le calcul de fréquence
2025-05-22 Modification de TX2 pour observer les trames de 2 esp différents
2025-05-22 Ajout d'une entete à la trame envoyée pour une future identification des données
2025-05-22 Passage à PlatformIO pour les programmes Arduino
2025-05-23 Ajout d'un nouveau programme RX pour l'envoi en série du temps écoulé lors de 5 réceptions
2025-05-26 Mis à jour du dossier, fréquence mise à 300Hz
2025-05-27 Ajout de la détection de la recharge de la batterie en USB
2025-06-02 Ajout de tous les codes qui permettent d'effectuer la communication RS485 et ESP NOW
2025-06-06 Ajout des fonctions d'envoi RS485 de plusieurs patchs vers le module de com
2025-06-16 Ajout des fonctions de communications interpatch en RS485, et com ESP NOW pour finir la chaîne de communication, envoi des 4 trames de 23 octets à 250 Hz
2025-06-16 Ajout des commentaires dans le fichier Python
2025-06-17 Respect de l'ordre de lecture des 4 capteurs de force pour chacun des patchs pour avoir l'ordre 1 2 3 4 des capteurs
2025-06-18 Ajout de la mesure du baromètre
2025-06-24 Ajout des modèles 3D
    [comModCase.stl, lectC3P4.stl, leftC1P1.stl, leftC1P2.stl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]
2025-06-30 Ajout de la fonctionnalité de commutation de signal depuis un programme python
    [rightC1P2.stl, rightC3P2.stl, rightC3P3.stl, rightC3P4.stl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]
2025-06-30 Fonction écriture des données dans un fichier CSV
    [output.csv, output2.csv]
2025-07-02 test de documentation
2025-07-02 Documentation impression 3D & assemblage
2025-07-02 Ajout de commentaires et des images
2025-07-03 Test de mise en page documentation
2025-07-07 Modifications pour la prise en compte de la semelle droite, meilleure conversion
2025-07-08 Documentation des fichiers de programmation
    [output.csv, output2.csv]
2025-07-08 Mise en forme des documentations
2025-07-08 Amélioration de la communication avec synchronisation sans trop de pertes de données
2025-07-09 Envoi top départ de lecture depuis l'esp32 de réception
2025-07-09 Amélioration du programme de décodage
2025-07-10 Optimisation du programme de décodage
2025-07-10 Ajout d'un main et d'arguments pour le programme python de décodage
2025-07-10 documentation acquisition des données
2025-07-10 Corrections pour ESP32
2025-07-11 Amélioration de la documentation
2025-07-11 Commentaires programme python de décodage
2025-07-11 Ajout de commentaires envoi4Patchs
2025-07-11 Ajout de datasheets
